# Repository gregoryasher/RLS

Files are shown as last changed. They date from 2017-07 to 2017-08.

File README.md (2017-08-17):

# Remote Lab System: Base Station
The Remote Lab System is a system designed for the University of Washington Bothell campus's Electrical Engineering department. This was a Capstone (or Senior) project that concluded our degrees at the University of Washington. We are a group of Computer Engineering students who were enrolled in the program from 2015 to 2017 when we graduated summer quarter. The development of this project was broken up into Spring and Summer quarter 2017.

# Starting Notes
When we chose this as our project we were initially informed the system did not function. At all. What we found towards the end of our first quarter was the system did not work because previous teams did not create or test any of the components or any code to do so. It became apparent we needed to completely redesign the system and create all the code.

We created a project and work schedule and dove in. These schedules were essential to the success of our project.

# Goals
This was the fourth iteration of the Base Station and our design goals were to: 
Add an additional Intronix LogicPort logic analyzer to support a maximum total of 68-channels
Add an 16-bit Analog-to-Digital Converter (ADC)
Improve heat dissipation from linear regulators
Design a stable chassis
Update Graphical User Interface (GUI)
Improve software robustness

# Purpose
The Remote Lab System is designed to allow students to work on lab experiments remotely away from campus, or the lab facilities. This system is a learning tool and study aid allowing students to have unlimited access, at any time of day, to their required lab equipment. Dr. Arnold Berger at the University of Washington Bothell conducted research showing that when students were given the ability to work remotely, the peak times were between midnight and 4:00 am. His research also concluded that female students spent more time connected to the system than male students, and also generally received higher grades on related course content.

While no version of the Remote Lab System has been officially implemented in coursework, we believe our project will increase students understanding of hardware integration by allowing them to quickly change various settings on daughterboard experiments and observe their changes in real time.

# Conclusion
At the end of our Capstone program in Summer quarter 2017 we had successfully achieved our goals. 

We added an additional logic analyzer: allowing the use of the two operating independently (two 34-channel logic analyzers) or dual support (one 68-channel logic analyzer) based on the configuration of the attached daughterboard.

We added a 16-bit ADC, effectively increasing the accuracy of node voltage measurements made by the system by 256 times.

We successfully solved the heat dissipation issue on the linear regulators by increasing the heatsink size and adding a thermally controlled fan circuit. 

We purchased and built a galvanized steel chassis for the system to be housed, complete with rubber feet to reduce vibrations caused by the fan. The motherboard's daughterboard connectors protrude from the lid such that no daughterboard will have clearance issues on the lid. The motherboard is mounted to the lid using brass standoffs threaded to the lid. The Velleman Oscilloscope/Function Generator system is securely mounted to the bottom of the chassis. Connector cables were made long enough such that the lid may be removed from the chassis and placed flat beside it. The fan is securely mounted to the chassis with no interference on the motherboard and in direct line with all four linear regulator heatsinks.

We successfully updated the GUI to improve security and user lockouts. The user can no longer send updated board information to a daughterboard not installed. The user can no longer change settings on a daughterboard not installed. The user is forced to check which board is installed before making any settings changes. 

The GUI now automatically detects the correct communications port for the Remote Lab System. If the Remote Lab System is not detected upon program start-up, a prompt appears warning the user.

Pressing the "Update Board" button now actually updates the board with the user's desired daughterboard settings.

Pressing the "Check Board" button now actually sends a request to read the daughterboard's boardID pin states. It also receives the correct values that were read.

Linear regulators now have supporting code and the values change based on the constructor's inputs. It should be noted that these devices in previous iterations never operated due to a lack of supporting code.

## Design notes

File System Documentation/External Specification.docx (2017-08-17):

# Remote Lab Station

BCE 496: Capstone Design 2

External Specification

Gregory Asher --- Student ID: 1566775

Gytautas Jankauskas --- Student ID: 1568743

Paolo Sebastian --- Student ID: 1573079

Andrew Soshea --- Student ID: 1321957

Introduction 3

User Guide 3

Hardware Specifications 4

Software Specifications 5

Graphical User Interface (GUI) 5

External Software 6

Operational Requirements 6

# Introduction

The University of Washington Bothell campus is a commuter campus meaning many students commute over a distance (sometimes long) to attend classes. The Remote Lab Station allows students to work on lab experiments at any time and from anywhere.

Using remote desktop applications, a student or faculty member is able to gain access to the Remote Lab Station and run experiments on the plugged in daughter boards. Daughter boards are lab experiments designed by other capstone groups that may give the ability to change node voltages, resistor values, and capacitor values in a circuit.

A user may connect remotely to the Remote Lab System. Upon connecting to the system, they have access to the the hardware on the computer where the Remote lab system is set up. They will have access to the Velleman Oscilloscope and Function Generator and will be able to run tests on real hardware in real time from the comfort of their own home. They will even be able to change values for the tests they are running to make sure they have everything they need to complete their lab.

Due to new restrictions from the UW-IT department, a VPN token (Husky OnNet) is required to connect to the UW campus network remotely. Refer to the UW IT Husky OnNet About Page (https://itconnect.uw.edu/connect/uw-networks/about-husky-onnet/) for more information.

# User Guide

The Remote Lab System Graphical User Interface (GUI) and Arduino software was tested on Windows 7 and Windows 10. We do not guarantee the software’s function on any platform.

In order to connect to use the Remote Lab System the user must connect to the correct campus workstation with the system plugged in. The student should obtain or be provided the workstation’s IP address by a leading faculty member.

Once there, an executable file named “RLS.exe” can be opened and experimentation may begin. To open the Oscilloscope and Function generator software, simply press the “Oscilloscope/Function Generator” button. To open one or both of the LogicPort software, press one of the corresponding “Logic Analyzer” buttons.

Before changing any of the settings in the GUI, a “Check Board” operation must be completed by pressing the “Check Board” button.

The “Update Board” button will again first verify the same board is still installed before sending the desired settings. If the same board is not installed, the user will be warned and updating will not be allowed. Otherwise, after verification, the updated settings will be transmitted to the Arduino.

# Hardware Specifications

- Chassis
  - Size - 10 in x 10 in x 6 in
  - Material - Galvanized Steel
  - Weight - 9lbs
- 2x rear connectors
  - One USB connector
  - One DIN5 power connector
- 1x 80mm Fan
- 4x 40 pin connectors
  - See Figure X for specific pin functions.
- 2-logic Analyzers
  - 68-channels possible
- Velleman Function Generator
  - Amplitude range: 100 mVpp to 10 Vpp @ 1 KHz
  - Offset: from 0 to -5 V or +5 V max
  - 8 bit vertical resolution
  - Sample rate: 12.5 MHz
  - 50 ohm output impedance
  - Frequency range: 0.005 Hz to 500 kHz
- Velleman Oscilloscope
  - Two channel DC bandwidth
  - 1 Mohm / 30 pF Input impedance
  - 30 V maximum input voltage
  - 10 mV to 3V/division input range
  - 0.3 mV display resolution
  - Records 4K samples / channel
  - Sampling frequency of 250 Hz to 25 MHz
- ADS1115 16-bit Analog-to-Digital Converter
  - 4-channels
    - Channel 0: +5 Volts max input
    - Channel 1: +15 Volts max input
    - Channel 2: -5 Volts max input
    - Channel 3: -15 Volts max input
- LT3015 Negative Linear Voltage Regulators
  - -1.22 Volts to -15 Volts output
  - Maximum 0.5 Amp output
  - .14 mV per step
  - Fused from power supply
- LT1963 Positive Linear Voltage Regulators
  - 1.21 Volts to +15 Volts output
  - Maximum 1 Amp output
  - .14 mV per step
  - Fused from power supply
- External power supply
  - Input - 120 VAC
  - Output
    - +15 Volts at 1.5 Amps
    - +5 Volts at 4 Amps
    - -15 Volts at 0.5 Amps
- Temperature range = 0°C - 70°C

# Software Specifications

Students will be able to connect to the RLS workstation via windows remote access to the IP: 128.208.255.52. A user may connect on campus or off campus using the Husky OnNet VPN. One user may to connect to the workstation at a time. On the desktop of the RLS workstation there is an executable file labeled “Remote Lab System”. This opens the RLS graphical user interface (GUI).

### Graphical User Interface (GUI)

Through the GUI, the user is able to check which daughter board is connected, change settings via drop down menus, send updated settings to the Arduino, open the logic analyzer software, and open Velleman oscilloscope software.

When the RLS software is first opened, daughter board settings menus are all deactivated. The only buttons available for interaction are “Check Board”, “Logic Analyzer 1”, and “Logic Analyzer 2”. This prevents a user from changing and applying settings when no daughter board, or a different daughter board, is connected.

A user must click the “Check Board” before any other interaction is possible. If no board is detected or the user has not checked board, then the user will not have permissions to changing any of the settings for any of the boards. Settings may only be changed for a board that is active.

Update board first makes sure that the board that the user is working on is actually the daughter board connected to the Arduino. If it is not, it prompts the user to check board again.

Window resizing including maximizing the screen is possible though the experiment window does not scale with window size.

### External Software

The buttons “Oscilloscope/Function Generator”, “Logic Analyzer”, and “Logic Analyzer 2” open their respective software. This software is provided by the respective manufacturers and is used to take measurements. A user is not allowed to open more than one process of each. If a user attempts to open one that is already open, they are told an instance is already running.

On exit, the software for the logic analyzers and oscilloscope/function generator are also all closed.

# Operational Requirements

In order to operate the system there are some key operational requirements. While this is a remote lab station designed to be used remotely, the Daughterboards must be physically cycled in and out in order for a user to change experiments. This may be done during business hours by a student or a staffed lab technician.

The Remote Lab Station requires an Electrical Engineering lab computer with the Velleman Oscilloscope and Function Generator software, the LogicPort Logic Analyzer software, and our Remote Lab Station software installed. This lab computer should not be used for any purpose other than the Remote Lab Station.

In order for the system to be operational, the Remote Lab Station computer is required to maintain an internet connection and be accessible remotely using the Husky OnNet VPN as required by UW-IT.

The remote lab system has an operating temperature range of 0°C - 70°C. It should be kept in a cool dry place and out of the sunlight. While direct sun exposure should have no effects on the system, the system does generate heat and should have the ventilation ports clear to allow for proper cooling.

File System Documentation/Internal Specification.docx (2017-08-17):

# Remote Lab Station

BCE 496: Capstone 2

Internal Specification

# Abstract

The Remote Lab System is an experimental system designed for electrical engineering students to connect and perform laboratory experiments remotely from off campus. This documentation contains details related to individual component usage including design schematics, algorithms, and graphical interface implementation.

Gregory Asher --- Student ID: 1566775

Gytautas Jankauskas --- Student ID: 1568743

Paolo Sebastian --- Student ID: 1573079

Andrew Soshea --- Student ID: 1321957

Abstract 1

Overall Design 4

Hardware Design 5

Hardware Operation 5

Logic Analyzer 5

Oscilloscope and Function Generator 6

Voltmeter 6

Linear Regulators 9

AD5293 Digital Potentiometers 9

Heat Dissipation 10

Software Design 11

Graphical User Interface (GUI) 11

External Software 12

Arduino 12

readBoardID() 12

Linear Regulator Shutdown 12

Safety Check 12

Daughterboard 13

Linear Voltage Regulator Control 13

Digital Potentiometer Control 13

Test Plan 14

Hardware 14

Individual and Independent Component Test Phase 14

LT1963 (Positive Linear Regulator) 14

LT3015 (Negative Linear Regulator) 15

ADS1115 16-bit ADC (on Adafruit breakout board) 15

AD5293 (Digital Potentiometer) 16

ULN2803A (Darlington Transistor Array) 16

RA30421051 16

LM337 (-5 Volt Regulator) 16

LM317 (+5 Volt Regulator) 16

Motherboard 16

Small Assembly Test Phase 17

Linear Regulator Circuit 17

LM337 and LM317 17

Cooling Circuit 17

Chassis 17

Final Assembly Test Phase 18

Software 19

White Box Software Testing 19

Black Box Software Testing 20

Project Schedule 21

Appendix A: Bill of Materials 22

Appendix B: System Parts List 23

Appendix C 24

# Overall Design

The Remote Lab System (RLS) has four essential components: the motherboard, experimental daughterboards, system enclosure, and dedicated workstation provided by UWB.

The RLS is remotely connected to by students enrolled at the University of Washington using Remote Desktop. Once the student is connected to the campus workstation attached experiments can be run using the RLS GUI. An system overview can be seen in Figure 1.

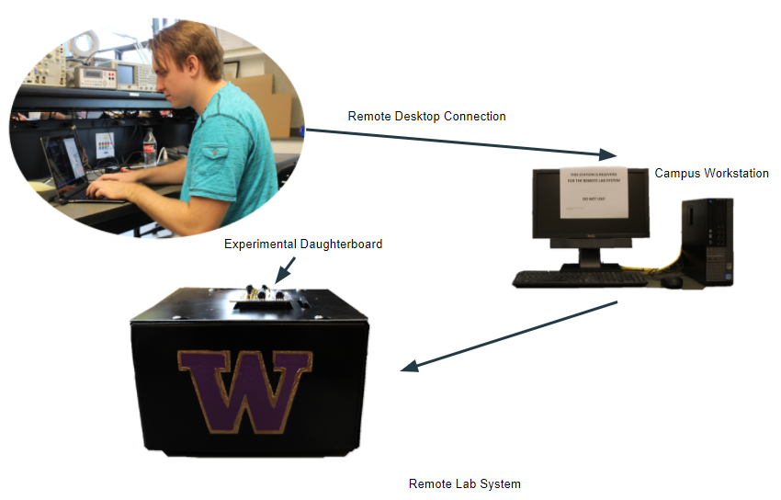
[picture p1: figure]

Figure 1: Overall system layout the Remote Lab System.

Contained within the system enclosure is a USB hub that connects an Arduino Mega 2560, two Intronix logic analyzers, and the Velleman oscilloscope and function generator to the campus workstation. Note: The Arduino Mega 2560 does not obtain power from the USB hub. Experimental boards plug into the RLS using 4 40-pin connectors on the top of the system enclosure.

# Hardware Design

A parts list can be found in Appendix A.

The Remote Lab System is enclosed in a galvanized chassis with a 80mm 2-pin PC fan mounted to the back of the enclosure. There are six connectors visible on the exterior of the chassis: one DIN 5-pin power supply connector, one USB connector, and 4 daughterboard connectors.

The system is powered by a switching mode power supply. This power supply has a DIN 5-pin connector supplying +5V at 4 Amps, -15V at 0.5 Amps, +15V at 1.5 Amps. Each of these pins are protected using a fuse on the motherboard corresponding to their rated voltages. Warning: It is possible to exceed the current limitation of the power supply if multiple linear regulators are used with a low resistance load (less than 1 kΩ). A maximum of one device should be in this mode at any given time.

The motherboard has 4 heat sinks aiding in the cooling of the LT3015 and LT1963 linear regulators. These heat sinks are partnered with an 80mm 5V fan to keep the devices cooled when in high current low voltage output mode.

Mounted to the chassis is a 5V chassis fan.

## Hardware Operation

Components of the motherboard are controlled using an Arduino Mega 2560. Supporting code has been written to control the digital potentiometers allowing users to change the linear regulator outputs. Additionally, supporting code has been written to allow users to control the oscilloscope probe gain. For specific usage of any supporting code, see the Software Operation section.

### Logic Analyzer

The logic analyzers implemented on the motherboard were designed by Intronix. The motherboard simply acts as a mount for these devices and passes the input pins through to the daughterboard connectors. In order to use the two logic analyzers together for a total of 68-channels, the daughterboard must provide a common clock and trigger for both devices. This allows the two logic analyzers to be used independently if desired. A user guide provided by Intronix for using multiple logic analyzers can be found in Appendix C. Additional support for the Intronix logic analyzers can also be found on their website.

### Oscilloscope and Function Generator

The oscilloscope and function generator implemented in the motherboard was designed by Velleman. The motherboard has connector pins allowing the channels of the oscilloscope and function generator to be mechanically fastened and routed to the daughterboard connectors. The scope probe gain adjustment circuit can be seen in Figure 3.

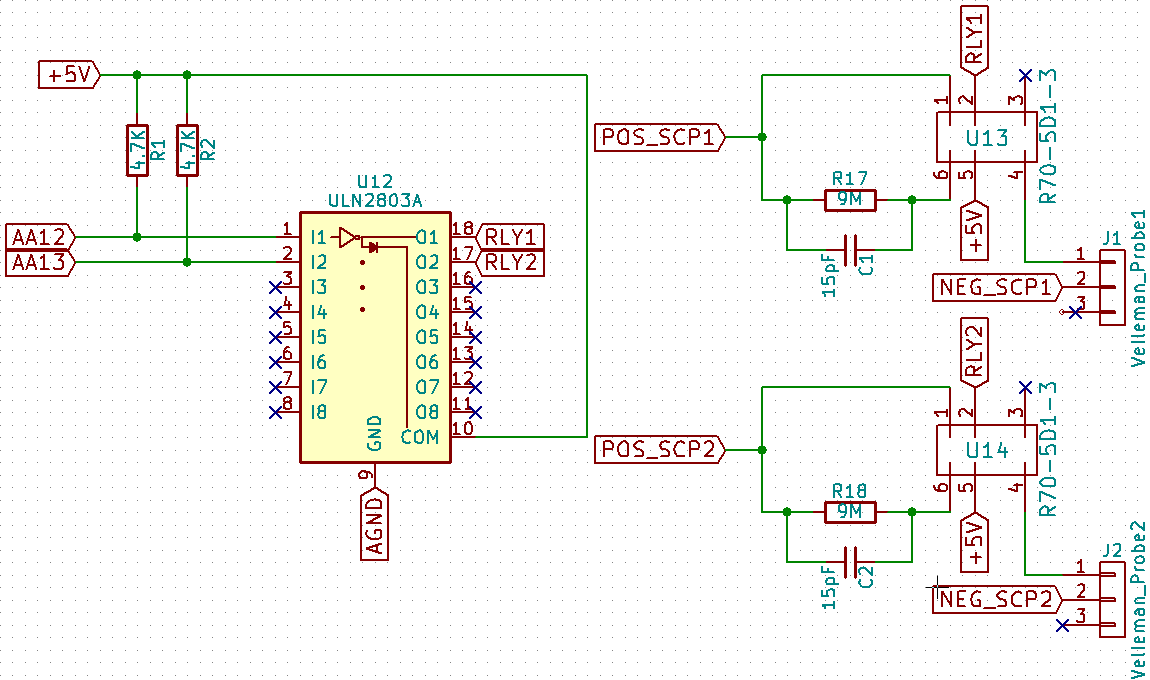
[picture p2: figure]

Figure 2: Scope probe gain schematic.

### Voltmeter

Implemented on the motherboard is an Adafruit ADS1115 4-channel 16-bit ADC. In single ended mode the ADC measures node voltages with respect to ground. The channels operate as follows:

- A0 valid for inputs 0V to +5 Volts
- A1 valid for inputs 0V to +15 Volts
- A2 valid for inputs -5V to 0 Volts
- A3 valid for inputs -15V to 0 Volts

Channels A1 and A3 operate using a voltage division circuit with a ratio of 3.

The voltage divider circuit reduces the voltage seen by the input protecting op-amp by a factor of 3. This allows an experimental board to measure voltages up to 15 volts. After a measurement is taken by the ADC, it is then multiplied by the voltage division ratio in order to obtain the actual value and then displayed to the user on the GUI.

The ADS1115 supports only positive voltages on the input pins in single ended mode so an inverting op-amp on the negative input pins of the ADS1115 (A2 and A3). Before the input voltage is inverted it also goes through a protection buffer with unity gain. The positive channels of the ADS1115 (A0 and A1) has an op-amp configured for unity gain as input protection.

Additional input protection for the ADC comes in the form of Schottky diodes. These diodes remove voltages greater than +5 volts and less than -5 volts. A circuit diagram of the inputs to the ADC can be seen in Figure 4, 5, 6, and 7.

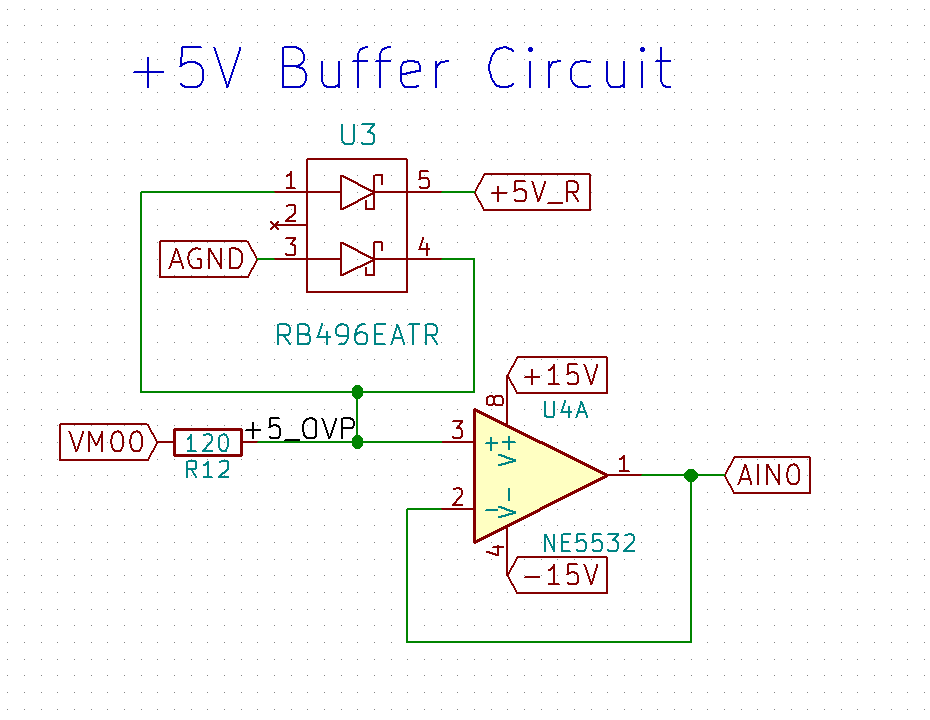
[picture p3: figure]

Figure 3: Positive 5 Volt buffer circuit schematic.

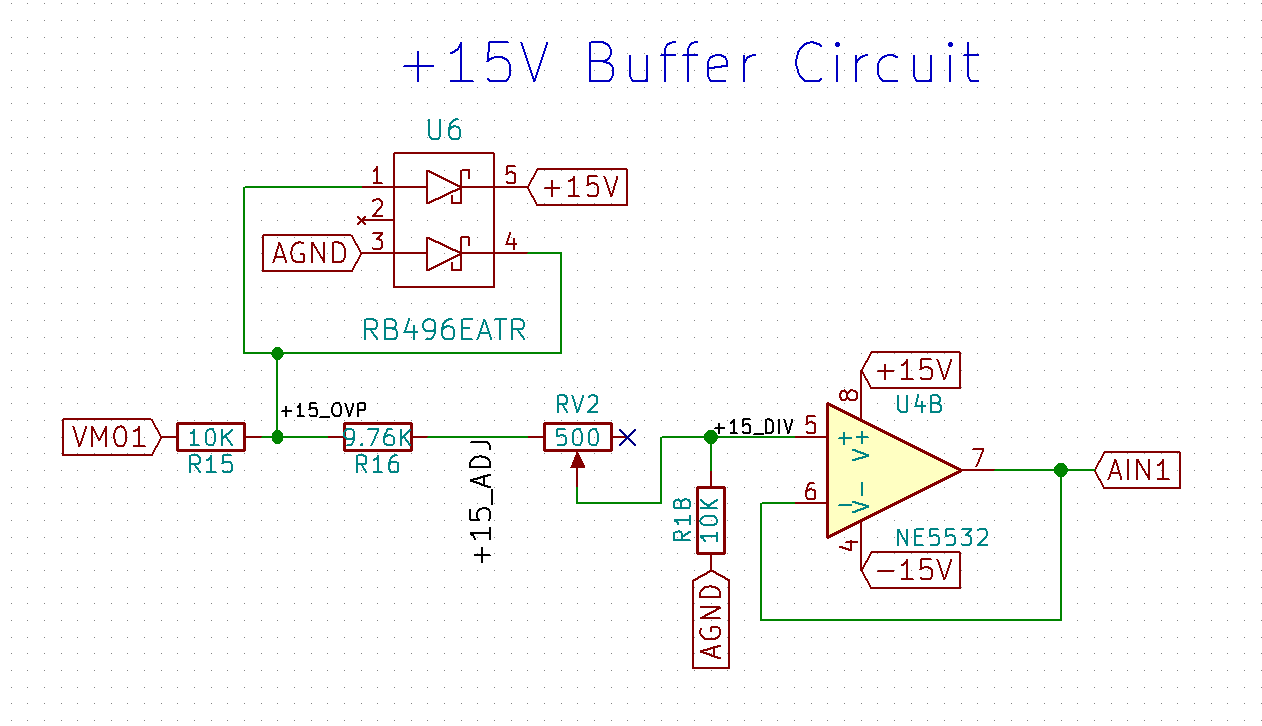
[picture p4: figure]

Figure 4: Positive 15 Volt voltage divider and buffer circuit schematic.

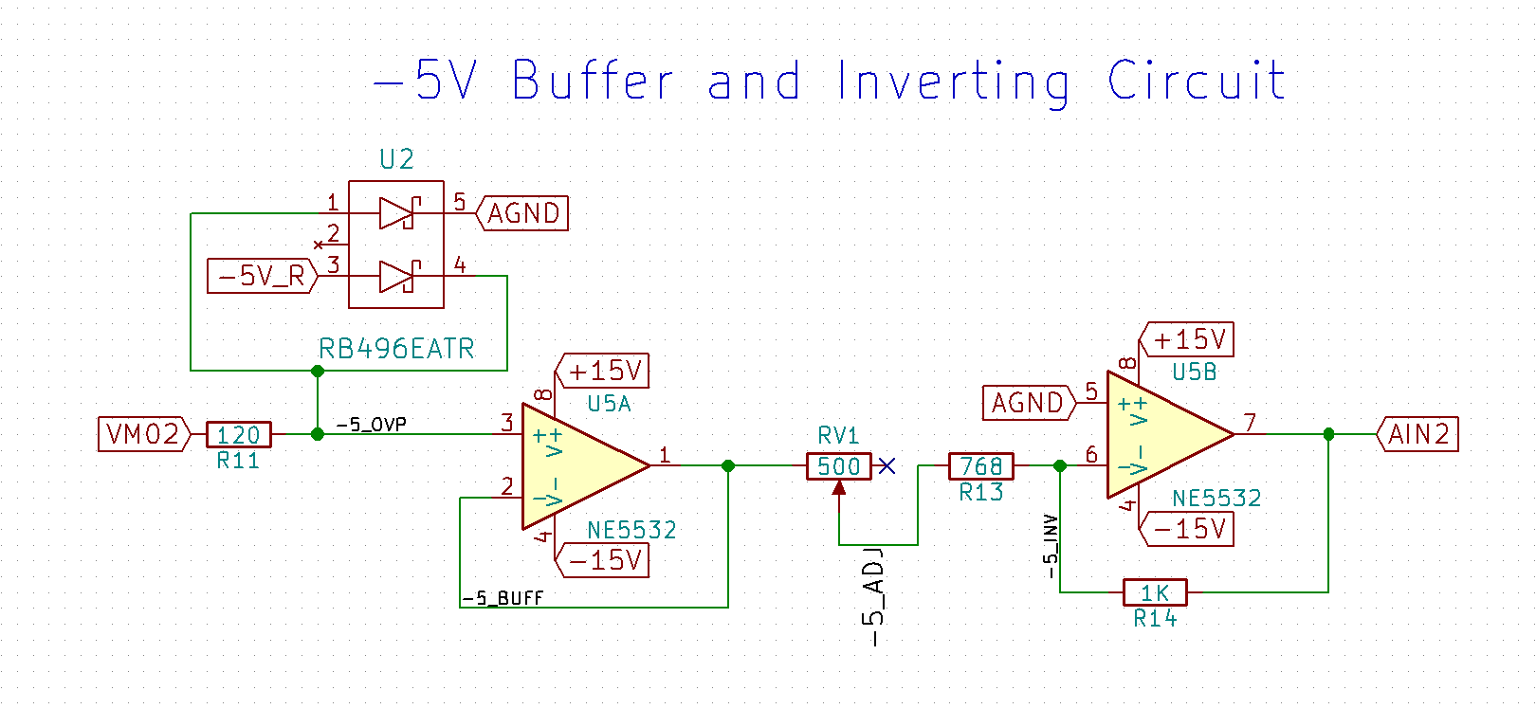
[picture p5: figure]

Figure 5: Negative 5 Volt inverter and buffer circuit schematic.

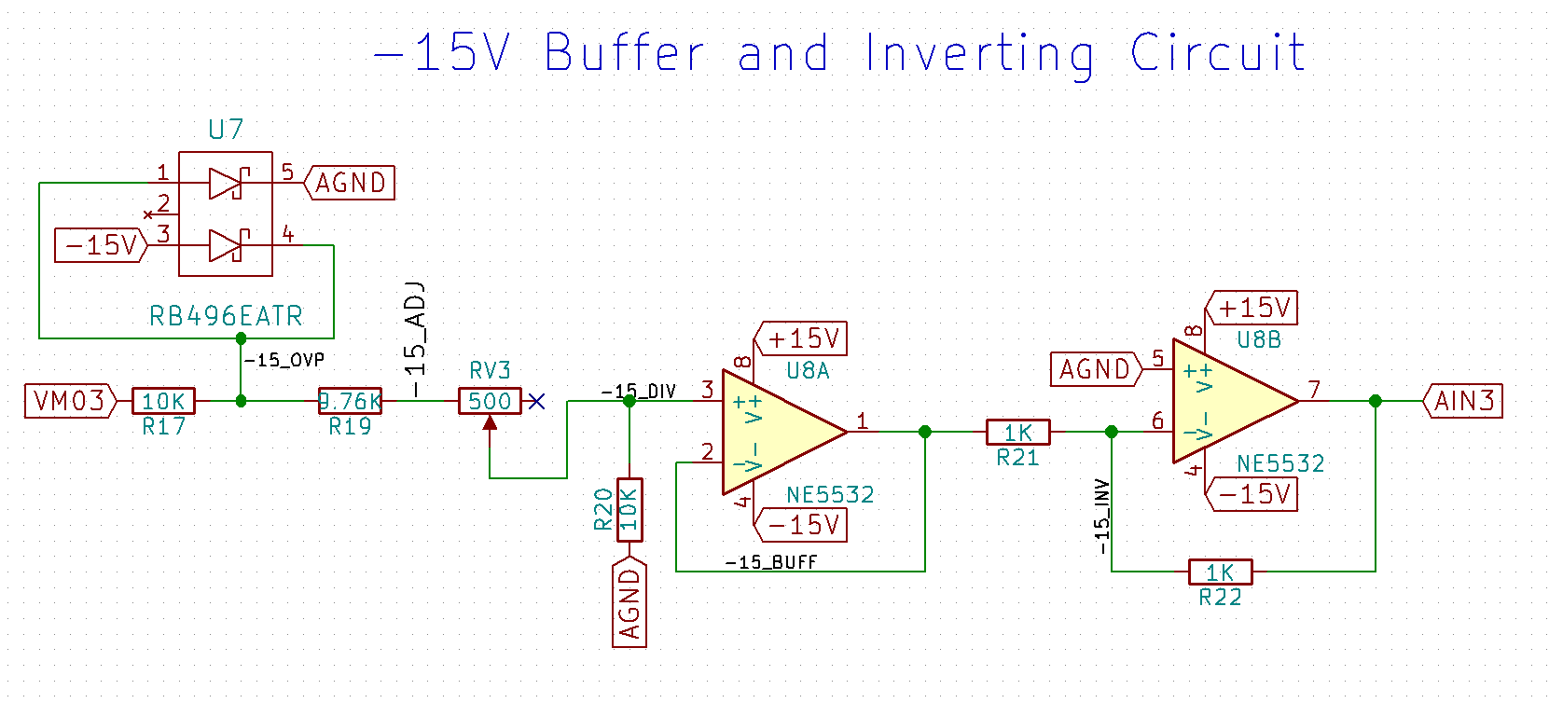
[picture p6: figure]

Figure 6: Negative 15 Volts voltage divider, inverter, and buffer circuit schematic.

### Linear Regulators

The motherboard contains 4 linear regulators: 2 negative regulators (LT3015) and 2 positive regulators (LT1963). A basic schematic, as taken from the datasheets, allowing adjustable operation can be seen in Figure 8 and Figure 9. In place of R2, our implementation has a 20kΩ digital potentiometer (AD5293). The output voltage from the linear regulators is based on the ratio of R1 and R2. With R1 at 1.78kΩ the entire output range of the linear regulators matches the full range of the digital potentiometer.

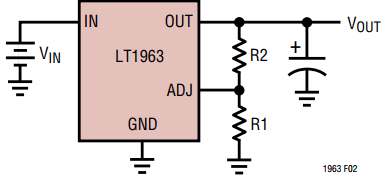
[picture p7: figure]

Figure 7: LT1963 with adjustable output as taken from datasheet.

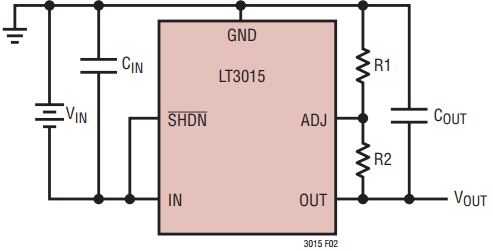
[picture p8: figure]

Figure 8: LT3015 with adjustable output as taken from datasheet.

### AD5293 Digital Potentiometers

Four AD5293 20kΩ digital potentiometers, one for each linear regulator, are used on the motherboard and control linear regulator’s output. The potentiometers are controlled using SPI communication (SPI Mode 1) from the Arduino. The AD5293 has a daisy chaining ability used in the motherboard design, one pair for each linear regulator pair (ie: one daisy chain for both LT3015’s and one daisy chain for both LT1963’s). This requires a 32-bit SPI transfer to change the resistance value.

### Heat Dissipation

The linear regulators are capable of supplying +1.21 Volts from the positive regulator, and -1.22 Volts from the negative regulator. If the attached load is low impedance, high current and high power is generated from the regulator. This heat is dissipated using the heat sinks and fan. Note: Only one linear regulator may be in this low voltage, low output impedance mode at any given time.

The heat sinks used on this motherboard are manufactured by Ohmite and have feet that need to be accounted for in PCB design. These feet should not be connected to any trace and should be isolated.

An 80mm fan is also included in the chassis for the system to force airflow through the heat sink fins. This fan circuit is powered by a MOSFET using a thermistor. The fan circuit diagram can be seen in Figure 10.

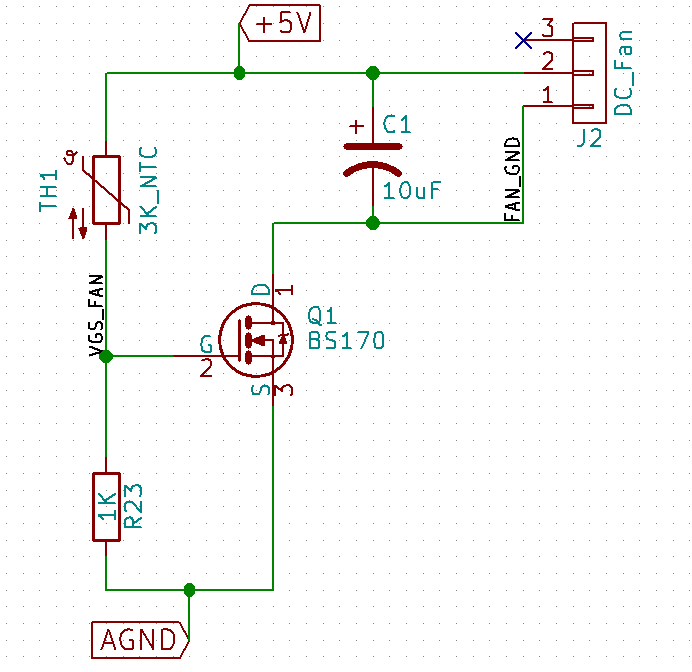
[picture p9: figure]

Figure 9: Fan circuit diagram.

# Software Design

Students will be able to connect to the RLS workstation via windows remote access to the ip: 128.208.255.52. A user may connect on campus or off campus using the Husky OnNet VPN. One user may to connect to the workstation at a time. On the desktop of the RLS workstation there is an executable file labeled “Remote Lab System”. This opens the RLS graphical user interface (GUI).

### Graphical User Interface (GUI)

The GUI is designed and programmed using Windows Forms C#. The GUI is used to communicate with the Arduino using UART serial communication. Through the GUI, the user is able to check which daughterboard is connected, change settings via drop down menus, send the updated settings to the Arduino, open logic analyzer software, and open oscilloscope software.

On startup, the COM port where the RLS system is connected is found and set. This allows the GUI to communicate with the Arduino at the request of the user without the user having to manually find the COM port that the RLS is connected to. This is done by checking all active COM ports and picking out the one the Arduino is connected to.

When the RLS software is first opened, daughterboard settings menus are deactivated using a deactivate function. The only buttons available for interaction are “Check Board”, “Logic Analyzer”, and “Logic Analyzer 2”. This prevents a user from changing and applying settings when no daughterboard, or a different daughterboard is connected.

A user must click the “Check Board” before any other interaction is possible. If no board is detected or the user has not checked board, then the user will not have permissions to changing any of the settings for any of the boards. Settings may only be changed for a board that is active. Check board works by sending “boardID” to the Arduino via the UART protocol. The Arduino then sends back the ID of the daughterboard currently connected. Based on the board connected, the panel for the test for that specific daughterboard is then enabled.

The “Update Board” button first verifies the daughterboard the user is attempting to update is still connected to the Remote Lab System. If it is not, the GUI prompts the user to press “Check Board” again. If the correct daughterboard is still connected, “Update Board” compiles the user’s settings into a String based on the state of the drop down menus and bubble options. After the String is created it is transmitted to the Arduino using Universal Asynchronous Receiver/Transmitter (UART).

Window resizing including maximizing the screen is possible though the experiment window does not scale with window size. This is due to previously designed experiment windows.

### External Software

The buttons “Oscilloscope/Function Generator”, “Logic Analyzer”, and “Logic Analyzer 2” open their respective software. The software is opened via hard coded file paths. This software is provided by the manufacturer and is used to take measurements. A user is not allowed to open more than one process of each. If a user attempts to open one that is already open, they are told an instance is already running.

On exit, the software for the logic analyzers and oscilloscope/function generator are also all closed. The windows are closed using the process.kill() command provided in C#.

### Arduino

On power on or after reset, the Arduino reads the boardID of a connected daughterboard, shuts down the linear regulators, and executes supporting daughterboard code (if one is connected). After it performs these setup functions the Arduino waits for data to be received from the GUI. The GUI sends data in the form of a String such as boardID, or a daughterboard settings String to be interpreted by supporting daughterboard code.

#### readBoardID()

If the String sent by the GUI is equivalent to “boardid” the Arduino reads the boardID pins (configured to be pins A0 - A7 on the Arduino) using digitalRead(). The boardID pins will read 1111_1111 if no daughterboard is connected (ie: the boardID pins are tied high). The read 8-bit boardID is converted to a string and is sent to the GUI using Universal Asynchronous Receiver/Transmitter (UART).

#### Linear Regulator Shutdown

The linear regulators have a logical shutdown pin that is toggled using the Arduino. The shutdown is commonly triggered when changing daughterboards or when no board is detected.

#### Safety Check

The purpose of the safety check function is to constantly check the state of the boardID pins. If the boardID pins change states the linear regulators are shut down.

#### Daughterboard

Each daughterboard has a supporting C++ class that configures the Arduino’s digital pins to its own unique specification. This class is called upon when updating the board using the “Update Board” button in the GUI. The GUI sends a String via UART containing information passed onto the class.

In order to determine which daughterboard class to call, the Arduino first creates a substring to determine which board it is receiving information for. The daughterboard class then further dissects the String sent by the GUI to set digital pins on the Arduino.

#### Linear Voltage Regulator Control

A daughterboard can manipulate a total of four DC voltage sources, two negative and two positive. The Arduino adjusts the voltages of the regulators by manipulating digital potentiometers attached to each regulator. Voltages are set using a constructor with the desired voltage(s) taken as parameters. The constructor takes the desired output voltage value and calculates the required digital potentiometer resistance using one of the equations below.

The calculation used for setting the positive regulator values can be seen in Equation 1.

The calculation used for setting the negative regulator values can be seen in Equation 2.

Equation 1: Potentiometer (Ω)=(V_(OUT) - 1.21V)/((1.21V)/(1.78kΩ) + 3µA)

Equation 2: Potentiometer (Ω)=(V_(OUT) + 1.22V)/((-1.22V)/(1.78kΩ) + 30nA)

#### Digital Potentiometer Control

The digital potentiometer acts as a controllable resistor to adjust the linear voltage regulators. In order for the digital potentiometer to set its wiper to the calculated resistance value, the resistance must first be digitally converted into 20 Ω increments to complement the 1024-position resolution of the AD5293 digital potentiometers. This was accomplished using Equation 3.

Equation 3: Digital Resistance (Ω) =(R_(POT))/(20000.0 Ω)⋅1024.0 positions

Once the required digital resistance is calculated, the wipers for the digital potentiometers are enabled and they are sent a complete 16-bit data-word using SPI. This 16-bit word is composed of two unused bits followed by four command bits that control the operation of the digital potentiometer and finally the 12 data bits which contain the calculated digital resistance position that the digital potentiometer wiper needs to be set to. As the digital potentiometers are daisy chained, the data needed to be sent twice (for a total of 32 bits being sent) in order to reach both potentiometers. When the data has been sent and the potentiometers are set, the output voltage of the linear regulators are subsequently changed once they are turned back on.

# Test Plan

The test plan is broken down into two separate categories, Hardware and Software.

## Hardware

The hardware section is split into testing phases. The individual and independent component phase is testing that is done solely using a single component at a time. The small assembly testing phase is testing done incorporating small components together and testing their connected usages. Final assembly testing is performed after the entire PCB is assembled.

### Individual and Independent Component Test Phase

The individual and independent component test phase refers to the testing of each individual device received. We tested each device for expected operation and usage. The goal of this testing phase is to learn and experiment with device operations.

#### LT1963 (Positive Linear Regulator)

- Tested in adjustable output mode example circuit from datasheet. (See Figure 8)
  - Observed output range from 1.21 Volts to 15 Volts using manually adjustable pot and 1.78kΩ 1% resistor.
    - Calculated expected output value using Equation 1.
- Observed high amp output (with 1Ω load resistor).
  - Noted in this mode risk of blowing power supply fuse.
  - Daughterboards should use caution when using the regulators in this mode. Power supply has 1.5 Amp rating. One device is capable of producing a >1 Amp draw alone.
- Tested power generation and heat dissipation with heatsinks
  - Noted temperatures uncooled >55°C
  - Device rated for 70°C
  - Determined air cooling necessary in order to obtain high amperage outputs.

#### LT3015 (Negative Linear Regulator)

- Tested in adjustable output mode using example circuit from datasheet (See Figure 9)
  - Observed output range from -1.22 Volts to -15 Volts using manually adjustable pot and 1.78kΩ 1% resistor.
    - Calculated expected output value using Equation 2.
  - Observed high amp output (with 1Ω load resistor).
    - Noted in this mode high risk of blowing power supply fuse.
    - Daughterboards should use caution when using the regulators in this mode. Power supply has 0.5 Amp rating. One device is capable of producing a >1 Amp draw alone.
- Tested power generation and heat dissipation with heatsinks
    - Noted temperatures uncooled >55°C
    - Device rated for 70°C
    - Determined air cooling necessary when in high amp output mode.

#### ADS1115 16-bit ADC (on Adafruit breakout board)

- Tested single ended and differential input modes
  - Observed negative voltages unreadable in single ended mode.
  - Observed built in protection circuit functionality.
    - When applying voltages out of range of the ADC, reads max range. When pushed further past readings on other channels misbehave.
  - Observed higher gain states at lower input voltages for more accurate voltage measurement.
- Tested single ended mode with voltage divider, buffer, and inverting amplifier
  - Observed accurate reading with voltage divider and buffer circuits.
    - Compared Serial Monitor readings with multimeter
  - Observed accurate readings with inverted negative voltage inputs.
    - Compared Serial Monitor readings with multimeter
    - Will need to be inverted in the software for user view
- Tested auto gain adjustments in software
  - Used power supply and multimeter to observe resolution changes.

#### AD5293 (Digital Potentiometer)

- Tested basic functions of a single device
  - Device operates using SPI communication
    - SPI Mode 1
  - Observed reset operation
    - Noted on reset the wiper moves to half (10kΩ)
  - Observed resistance change based on hex values
    - Single device requires a 16-bit transfer
    - 10-bits are data (1023 possible wiper positions)
    - Each data bit accounts for ~20Ω
- Tested daisy chain capabilities
  - Requires 32-bit data transfer to write and update both devices
  - Observed resistance changes of both devices in series
    - Despite 32-bit transfer doesn’t appear slower

#### ULN2803A (Darlington Transistor Array)

- Tested outputs given 5 Volt inputs
  - Expected output currents large enough to drive inductive load
    - Able to toggle RA30421051 Relay

#### RA30421051

- Tested with DC power supply and pull up resistor
- Tested for continuity on switching poles
  - Expected switch to throw on 5 Volt logic

#### LM337 (-5 Volt Regulator)

- Tested with DC power supply with 15 Volt input
  - Expected consistent +5 Volt output

#### LM317 (+5 Volt Regulator)

- Tested with DC power supply with -15 Volt input
  - Expected consistent -5 Volt ouput

#### Motherboard

- Upon arrival performed visual inspection of quality
- Upon arrival measured resistance at all power nodes to all ground nodes.
  - Expected reading: Overload

### Small Assembly Test Phase

The small assembly test phase refers to the testing of multiple components tied together in a similar manner that will be used in the final implementation.

#### Linear Regulator Circuit

Two LT3015 and two LT1963 linear voltage regulators used in combination with 4 AD5293 digital potentiometers. For the two LT3015 negative linear voltage regulators two AD5293 digital potentiometers are daisy chained together.

- Tested voltage changes based on digital pot value changes
  - Observed full voltage output range (-15 Volts to -1.22 Volts)
- Tested software controller for changing voltage values
  - Observed correct operation based on function parameters
  - Function takes in a desired voltage and uses an algorithm to determine required digital potentiometer value

#### LM337 and LM317

- Tested to ensure expected output
  - Observed +15 Volt regulated down to +5 Volt output
    - Noted higher currents possible with lower impedance loads.
  - Observed -15 Volt regulated down to -5 Volt output
    - Noted higher currents possible with lower impedance loads.

#### Cooling Circuit

The cooling circuit operates using a BS170 N-Channel MOSFET, a thermistor, and a 5V 2-pin 80mm fan. The fan is implemented to encourage airflow along the heat sinks for the linear voltage regulators.

- Tested fan circuit with potentiometer to simulate thermistor
  - Expected to voltage drop across transistor to increase, thus turning on the fan
  - Observed fan operation

#### Chassis

- Tested connection fitment
- Tested daughterboard connector fitment against lid

### Final Assembly Test Phase

The final assembly test phase refers to testing after construction of the entire PCB (ie: all components have been soldered to the board). This testing is also performed after chassis modification has been completed.

- Tested motherboard spacer fitment on lid
  - Daughterboard connectors protrude from lid as expected
  - Reasonable connector clearance
  - Minimal flex experienced when attaching/detaching a daughterboard
- Tested connection to logic analyzer cards
  - Logic analyzers securely fastened to motherboard
  - Logic analyzer’s USB connector is accessible
- Tested Velleman connections
  - Mechanical probe connections are secure
  - Oscilloscope appropriately displays waveform
    - Waveform generated by Tektronix AFG3252 Waveform Generator
    - Waveform passed into scope via daughterboard oscilloscope probe pins
  - Function Generator produces acceptable waveform
    - Waveform measured by Tektronix MSO3012 Mixed Signal Oscilloscope
    - Waveform measured from daughterboard connector pin
- Tested USB hub connectivity with work station
  - Velleman is detected via USB hub
    - Velleman software receives hardware response
  - Logic analyzers are detected via USB hub
    - LogicPort software detects both devices independently
  - Arduino is detected via USB hub
    - Arduino detected by Arduino IDE
    - Communicates with GUI
- Test linear voltage regulator outputs
  - Positive regulators
    - Expected output ranges between 1.22 Volts and 15 Volts
    - Expected steady output at specified value
      - Measured using Keithley Multimeter
  - Negative regulators
    - Expected output ranges between -15 Volts and -1.23 Volts
    - Expected steady output at specified value
      - Measured using Keithley Multimeter
- Tested heat dissipation performance
  - Expected fan to power on when heat is detected
  - Expected device(s) to continue operating (ie: device does not enter shut down mode)
  - Device remains within operating temperature range
- Tested boardID detection
  - Expected 1111_1111 reading with no daughterboard connected
  - Simulated boardID’s using Keithley DC power supply

## Software

The Remote Lab System Graphical User Interface (GUI) and Arduino software was tested on Windows 7 and Windows 10. We do not guarantee the software’s function on any platform.

Software testing occurs in multiple stages throughout the development process and was performed both as White Box testing and Black Box testing. White box testing was used for evaluating the performance of code used for controlling essential devices. Black box testing was used to ensure limitations on user access and control of the system.

### White Box Software Testing

- Tested collection of user settings
  - Expected GUI to generate a String with user settings
  - Expected GUI to transmit created string using UART to Arduino
- Tested user lockout methods
  - Expected user can only change values of the active board
  - Expected all drop down menus inaccessible when no board detected
  - Expected warning message if no board detected
  - Required successful boardID check before settings can be changed
  - Only single instances of applications allowed
- Tested application shutdown on GUI exit
  - Expected LogicPort and Velleman software to terminate on GUI exit
- Tested communication from GUI to Arduino
  - User settings on the experiments page are correctly sent to the Arduino
    - Arduino handles these UART signals and passes them correctly to the corresponding daughterboard experiment C++ file.
  - boardID request sent via UART to Arduino
    - Arduino responds with boardID read from analog pins
- Tested automatic detection of RLS Arduino
  - Expected automatic port setting for Serial communication
- Tested Arduino control of linear regulators
  - Uses daisy chained AD5293 digital potentiometers
  - Expected outputs from LT3015 negative linear regulators to be from -15 Volts to -1.22 Volts
    - Error returned on out-of-range inputs
  - Expected outputs from LT1963 negative linear regulators to be from 15 Volts to 1.21 Volts
    - Error returned on out-of-range inputs
- Tested ADS1115 (ADC) control
  - Expected less than 1% margin of error
    - Simulated using Keithley DC power supply
    - Compared readings with Keithley multimeter
  - Expected single ended single readings
- Tested Arduino safety functions
  - Arduino shuts down linear regulators on GUI exit
  - Arduino shuts down linear regulators when no boardID detected

### Black Box Software Testing

- Tested Graphical User Interface (GUI)
  - User is unable to change settings when daughterboard is not detected
  - User is only able to change settings on detected daughterboard screen
  - Software closes upon closing of the RLS GUI
  - User is only able one instance of each program
  - User can change detected daughterboard’s settings and observe correct output corresponding with the input settings

# Project Schedule

Schedule for Capstone 1:

| Category | Milestone | Due Date
1. | Documentation | Determine Parts to be Used | May 19th 2017
2. | Documentation | Final Contract | June 9th 2017
3. | Documentation | Final Project Specification | June 9th 2017

Schedule for Capstone 2:

| Category | Milestone | Due Date
1. | Hardware & Software | Demonstrate New Motherboard Design | July 28th 2017
2. | Hardware & Software | Integrate Daughterboards with Motherboard | July 28th 2017
3. | Documentation | Final Report | August 18th 2017
4. | Documentation | Final Presentation | August 18th 2017

# Appendix A: Bill of Materials

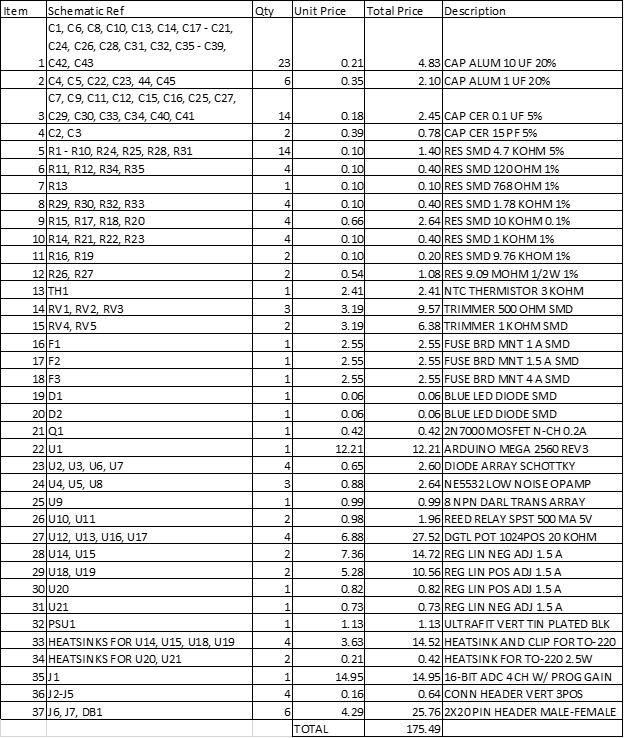
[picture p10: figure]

# Appendix B: System Parts List

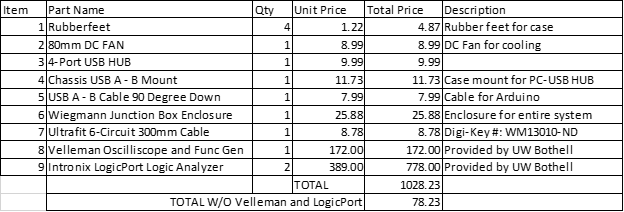
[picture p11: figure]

# Appendix C

The following is copied from a .txt file provided by Intronix on the usage of multiple logic analyzers together.

As mentioned in the FAQs, it is recommended to use multiple units in state mode if your circuit can provide a common clock and trigger signal to all units. The common clock is what keeps the samples coherent in time, while the common trigger signal is what synchronizes the acquisitions of multiple units.

It is possible to use multiple units in timing mode, but keep in mind that each unit has its own independent clock oscillator. Since the clocks are not synchronized this means that at the trigger sample there will be an uncertainty of +/-1 sample period between units. This effectively reduces the timing resolution by 1/2 (500MHz only has resolution of 250MHz). With compression enabled, the situation can get even worse since it may be possible to compress large numbers of samples into the buffer. While the uncertainty at the trigger point is always +/-1 sample period, the clock oscillators have a worst case mismatch of 100ppm between multiple units. If you were able to compress 1,000,000 samples into the buffer, the signals sampled 1,000,000 sample periods before/after the trigger event could have a differential error of 100 sample periods between units! This is why we don't recommend using multiple units in timing mode. Often times you won't be able to capture (or even be interested in) 1,000,000 samples, so this last point isn't always an issue.

Here are a few tips on using multiple LogicPorts from one PC:

1. The LogicPort software will open the first LogicPort it finds. The first instance of the software you open will use the first LogicPort you connected to the PC. Once that instance is open, the second instance of the software will find and use the second LogicPort connected and so on.

2. It will be more convenient if you have separate installations of the LogicPort software so that each instance has it's own .INI file in it's respective install directory. The .INI file tells the software which project file to open when the application starts up (among other things). The default installation is in:

"C:\Program Files\LogicPort"

We recommend that you install the second instance in a directory such as:

"C:\Program Files\LogicPort2"

3. Here's the tricky part: The second installation will overwrite the desktop and start menu shortcuts causing them to point to the second installation only. You will need to create a new shortcut which points to the first installation. You should be able to just make a copy of the desktop shortcut and change the shortcut's target directory to point to the first installation.

Note that although there should be separate installations, you don't necessarily need to use separate directories for project or export files. For example, you could open a project file in the "\Projects" directory of the first installation using the second instance of the software.

We have run as many as 4 LogicPorts from the same PC simultaneously, and the theoretical limit is 127 units.

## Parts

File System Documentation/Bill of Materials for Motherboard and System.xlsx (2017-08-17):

Item | Schematic Ref | Qty | Unit Price | Total Price | Description | Part Name | Digi-Key Part # | Manufacuter | Package/Case | Link
1 | C1, C6, C8, C10, C13, C14, C17 - C21, C24, C26, C28, C31, C32, C35 - C39, C42, C43 | 23 | 0.21 | 4.83 | CAP ALUM 10 UF 20% |  | PCE3895CT-ND | Panasonic Electronic Components | RADIAL SMD 4x5.3mm | https://www.digikey.com/products/en?keywords=PCE3895CT-ND | Greg | Gytatus | Paolo | Andrew
2 | C4, C5, C22, C23, 44, C45 | 6 | 0.35 | 2.10 | CAP ALUM 1 UF 20% |  | PCE4024CT-ND | Panasonic Electronic Components | RADIAL SMD 4x5.3mm | https://www.digikey.com/products/en?keywords=PCE4024CT-ND | 110 | 130 | 120 | 100
3 | C7, C9, C11, C12, C15, C16, C25, C27, C29, C30, C33, C34, C40, C41 | 14 | 0.17 | 2.45 | CAP CER 0.1 UF 5% |  | 399-1250-1-ND | KEMET | 1206 | https://www.digikey.com/products/en?keywords=399-1250-1-ND
4 | C2, C3 | 2 | 0.39 | 0.78 | CAP CER 15 PF 5% |  | 490-9071-1-ND | Murata Electronics NA | THRU-HOLE | https://www.digikey.com/product-detail/en/murata-electronics-north-america/RDE5C2A150J0S1H03A/490-9071-1-ND/4772233
5 | R1 - R10, R24, R25, R28, R31 | 14 | 0.10 | 1.40 | RES SMD 4.7 KOHM 5% |  | 311-4.7KERCT-ND | Yageo | 805 | https://www.digikey.com/product-detail/en/yageo/RC1206JR-074K7L/311-4.7KERCT-ND/732242
6 | R11, R12, R34, R35 | 4 | 0.10 | 0.40 | RES SMD 120 OHM 1% |  | P120FCT-ND | Panasonic Electronic Components | 1206 | https://www.digikey.com/products/en?keywords=P120FCT-ND
7 | R13 | 1 | 0.10 | 0.10 | RES SMD 768 OHM 1% |  | P768FCT-ND | Panasonic Electronic Components | 1206 | https://www.digikey.com/products/en?keywords=P768FCT-ND
8 | R29, R30, R32, R33 | 4 | 0.10 | 0.40 | RES SMD 1.78 KOHM 1% |  | P1.78KFCT-ND | Panasonic Electronic Components | 1206 | https://www.digikey.com/products/en?keywords=P1.78KFCT-ND
9 | R15, R17, R18, R20 | 4 | 0.66 | 2.64 | RES SMD 10 KOHM 0.1% |  | P10KBCCT-ND | Panasonic Electronic Components | 1206 | https://www.digikey.com/products/en?keywords=P10KBCCT-ND
10 | R14, R21, R22, R23 | 4 | 0.10 | 0.40 | RES SMD 1 KOHM 1% |  | P1.00KFCT-ND | Panasonic Electronic Components | 1206 | https://www.digikey.com/products/en?keywords=P1.00KFCT-ND
11 | R16, R19 | 2 | 0.10 | 0.20 | RES SMD 9.76 KHOM 1% |  | P9.76KFCT-ND | Panasonic Electronic Components | 1206 | https://www.digikey.com/products/en?keywords=P9.76KFCT-ND
12 | R26, R27 | 2 | 0.54 | 1.08 | RES 9.09 MOHM 1/2W 1% |  | PPCHF9.09MCT-ND | Vishay BC Components | THRU-HOLE | https://www.digikey.com/product-detail/en/vishay-bc-components/HVR3700009094FR500/PPCHF9.09MCT-ND/720088
13 | TH1 | 1 | 2.41 | 2.41 | NTC THERMISTOR 3 KOHM |  | 615-10008-ND | US Sensor | THRU-HOLE | https://www.digikey.com/products/en/sensors-transducers/temperature-sensors-ntc-thermistors/508?k=615-1008-ND
14 | RV1, RV2, RV3 | 3 | 3.19 | 9.57 | TRIMMER 500 OHM SMD |  | 490-2671-1-ND | Bourns Inc | J LEAD SMD | https://www.digikey.com/products/en?keywords=490-2671-1-ND
15 | RV4, RV5 | 2 | 3.19 | 6.38 | TRIMMER 1 KOHM SMD |  | 490-2660-1-ND | Bourns Inc | J LEAD SMD | https://www.digikey.com/products/en?keywords=490-2660-1-ND
16 | F1 | 1 | 2.55 | 2.55 | FUSE BRD MNT 1 A SMD |  | F1222CT-ND | Littelfuse Inc | 2-PAD SMD | https://www.digikey.com/products/en/circuit-protection/fuses/139?k=F1222CT-ND
17 | F2 | 1 | 2.55 | 2.55 | FUSE BRD MNT 1.5 A SMD |  | F1223CT-ND | Littelfuse Inc | 2-PAD SMD | https://www.digikey.com/products/en/circuit-protection/fuses/139?k=F1223CT-ND
18 | F3 | 1 | 2.55 | 2.55 | FUSE BRD MNT 4 A SMD |  | F1227CT-ND | Littelfuse Inc | 2-PAD SMD | https://www.digikey.com/product-detail/en/littelfuse-inc/0154004.DR/F1227CT-ND/183376
19 | D1 | 1 | 0.06 | 0.06 | BLUE LED DIODE SMD |  |  | Chanzon | 603 | https://www.amazon.com/Chanzon-Colors-100pcs-Emitting-Yellow/dp/B01CUGA380
20 | D2 | 1 | 0.06 | 0.06 | BLUE LED DIODE SMD |  |  | Chanzon | 603 | https://www.amazon.com/Chanzon-Colors-100pcs-Emitting-Yellow/dp/B01CUGA380
21 | Q1 | 1 | 0.42 | 0.42 | 2N7000 MOSFET N-CH 0.2A | 2N7000 | 2N7000TACT-ND | Fairchild/ON Semiconductor | TO-92 | https://www.digikey.com/product-detail/en/fairchild-on-semiconductor/2N7000TA/2N7000TACT-ND/3042479
22 | U1 | 1 | 12.21 | 12.21 | ARDUINO MEGA 2560 REV3 |  |  | Elegoo | SEE PCB FOOTPRINT | https://www.amazon.com/Elegoo-Board-ATmega2560-ATMEGA16U2-Arduino/dp/B0719HSWQ4?s=electronics
23 | U2, U3, U6, U7 | 4 | 0.65 | 2.60 | DIODE ARRAY SCHOTTKY | 2 Indep Schottky | RB496EACT-ND | Rohm Semiconductor | SOT-23-5 | https://www.digikey.com/products/en?keywords=RB496EACT-ND
24 | U4, U5, U8 | 3 | 0.88 | 2.64 | NE5532 LOW NOISE OPAMP | NE5532 | 296-13622-1-ND | Texas Instruments | SOIC-8 | https://www.digikey.com/products/en?keywords=296-13622-1-ND
25 | U9 | 1 | 0.99 | 0.99 | 8 NPN DARL TRANS ARRAY | ULN2803A | 497-2356-5-ND | STMircoelectronics | DIP-18 | https://www.digikey.com/product-detail/en/stmicroelectronics/ULN2803A/497-2356-5-ND/599591
26 | U10, U11 | 2 | 0.98 | 1.96 | REED RELAY SPST 500 MA 5V | HE721A0500 | HE100-ND | Littelfuse Inc | DIP-14 | https://www.digikey.com/product-detail/en/littelfuse-inc/HE721A0500/HE100-ND/133183
27 | U12, U13, U16, U17 | 4 | 6.88 | 27.52 | DGTL POT 1024POS 20 KOHM | AD5293 | AD5293BRUZ-20-RL7CT-ND | Analog Devices Inc | TSSOP-14 | https://www.digikey.com/product-detail/en/analog-devices-inc/AD5293BRUZ-20-RL7/AD5293BRUZ-20-RL7CT-ND/3790133
28 | U14, U15 | 2 | 7.36 | 14.72 | REG LIN NEG ADJ 1.5 A | LT3015 | LT3015IT#PBF-ND | Linear Technology | TO-220-5 | https://www.digikey.com/products/en?keywords=LT3015IT%23PBF-ND
29 | U18, U19 | 2 | 5.28 | 10.56 | REG LIN POS ADJ 1.5 A | LT1963 | LT1963ET#PBF-ND | Linear Technology | TO-220-5 | https://www.digikey.com/products/en?keywords=LT1963ET%23PBF-ND
30 | U20 | 1 | 0.82 | 0.82 | REG LIN POS ADJ 1.5 A | LM317 | LM317TFS-ND | Fairchild/ON Semiconductor | TO-220-3 | https://www.digikey.com/products/en?keywords=LM317TFS-ND
31 | U21 | 1 | 0.73 | 0.73 | REG LIN NEG ADJ 1.5 A | LM337 | LM337TFS-ND | Fairchild/ON Semiconductor | TO-220-3 | https://www.digikey.com/products/en?keywords=LM337TFS-ND
32 | PSU1 | 1 | 1.13 | 1.13 | ULTRAFIT VERT TIN PLATED BLK | On-board Power Plug | WM11778-ND | Molex, LLC | SEE PCB FOOTPRINT | https://www.digikey.com/products/en?keywords=WM11778-ND
33 | HEATSINKS FOR U14, U15, U18, U19 | 4 | 3.63 | 14.52 | HEATSINK AND CLIP FOR TO-220 | LARGE HEATSINK | C220-025-1AE-ND | Ohmite | SEE PCB FOOTPRINT | https://www.digikey.com/products/en?keywords=C220-025-1AE-ND
34 | HEATSINKS FOR U20, U21 | 2 | 0.21 | 0.42 | HEATSINK FOR TO-220 2.5W | LOW PROFILE HS | HS115-ND | Aavid Thermalloy |  | https://www.digikey.com/product-detail/en/aavid-thermalloy/507302B00000G/HS115-ND/5849
35 | J1 | 1 | 14.95 | 14.95 | 16-BIT ADC 4 CH W/ PROG GAIN | ADS1115 |  | Adafruit | 1X10 HEADER 2.54mm Pitch | https://www.adafruit.com/product/1085
36 | J2-J5 | 4 | 0.16 | 0.64 | CONN HEADER VERT 3POS |  | A19470-ND | TE Connectivity AMP Connectors | 1X3 HEADER 2.54mm Pitch
37 | J6, J7, DB1 | 6 | 4.29 | 25.76 | 2X20 PIN HEADER MALE-FEMALE |  |  |  | 2X20 HEADER 2.54mm Pitch | https://www.amazon.com/gp/product/B01ITMN6K6
 |  |  | TOTAL | 175.49
Item | Part Name | Qty | Unit Price | Total Price | Description | Link
1 | Rubberfeet | 4 | 1.22 | 4.87 | Rubber feet for case | https://www.amazon.com/gp/product/B003B0YDRM
2 | 80mm DC FAN | 1 | 8.99 | 8.99 | DC Fan for cooling | https://www.amazon.com/gp/product/B00ZFPDAI4
3 | 4-Port USB HUB | 1 | 9.99 | 9.99 |  | https://www.amazon.com/gp/product/B00XMD7KPU
4 | Chassis USB A - B Mount | 1 | 11.73 | 11.73 | Case mount for PC-USB HUB | https://www.amazon.com/gp/product/B003VSXQVI
5 | USB A - B Cable 90 Degree Down | 1 | 7.99 | 7.99 | Cable for Arduino | https://www.amazon.com/gp/product/B0716WBP9R
6 | Wiegmann Junction Box Enclosure | 1 | 25.88 | 25.88 | Enclosure for entire system | https://www.newegg.com/Product/Product.aspx?Item=9SIA5D52J56093
7 | Ultrafit 6-Circuit 300mm Cable | 1 | 8.78 | 8.78 | Digi-Key #: WM13010-ND | https://www.digikey.com/products/en?keywords=WM13010-ND
8 | Velleman Oscilliscope and Func Gen | 1 | 172.00 | 172.00 | Provided by UW Bothell | https://www.amazon.com/Velleman-PCSGU250-Usb-Pc-Scope-Generator/dp/B006DXCO3E
9 | Intronix LogicPort Logic Analyzer | 2 | 389.00 | 778.00 | Provided by UW Bothell | https://www.pctestinstruments.com/order.htm
 |  |  | TOTAL | 1028.23
 | TOTAL W/O Velleman and LogicPort |  |  | 78.23

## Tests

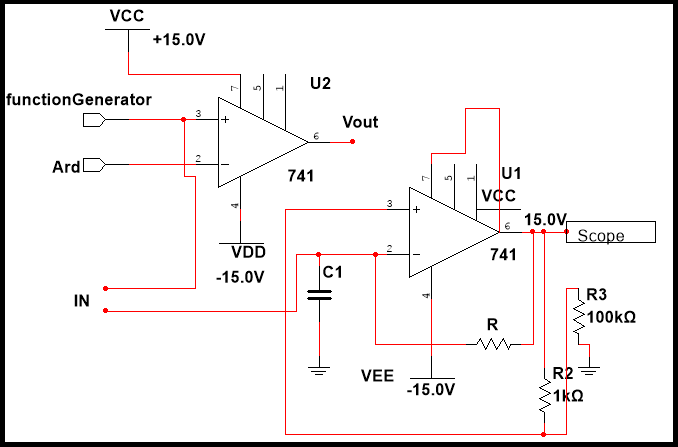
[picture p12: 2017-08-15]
RLSinC#/Remote_EE_Lab/Remote_EE_Lab/Resources/Experiment 93.png

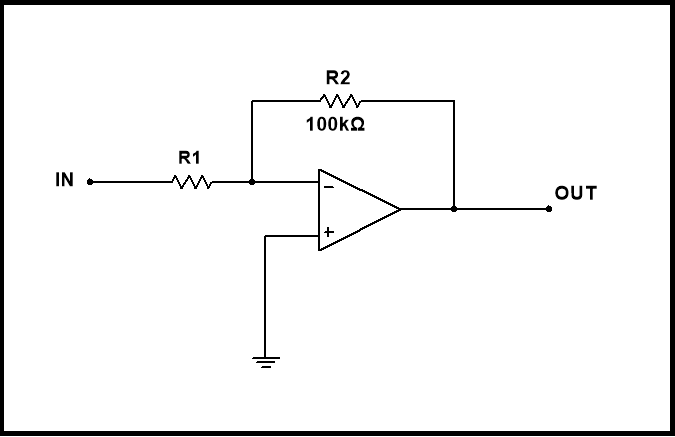
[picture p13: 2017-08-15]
RLSinC#/Remote_EE_Lab/Remote_EE_Lab/Resources/Experiment 11.png

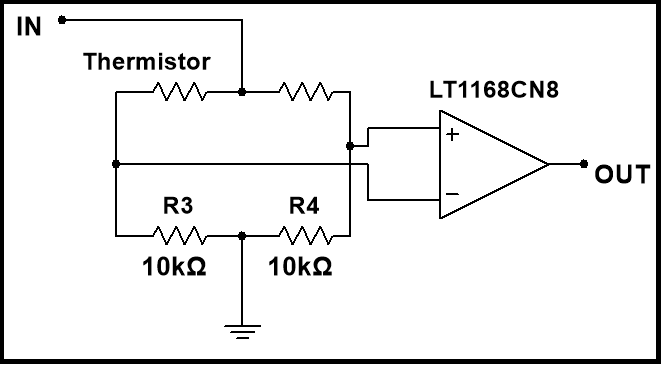
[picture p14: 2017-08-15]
RLSinC#/Remote_EE_Lab/Remote_EE_Lab/Resources/Experiment 81.png

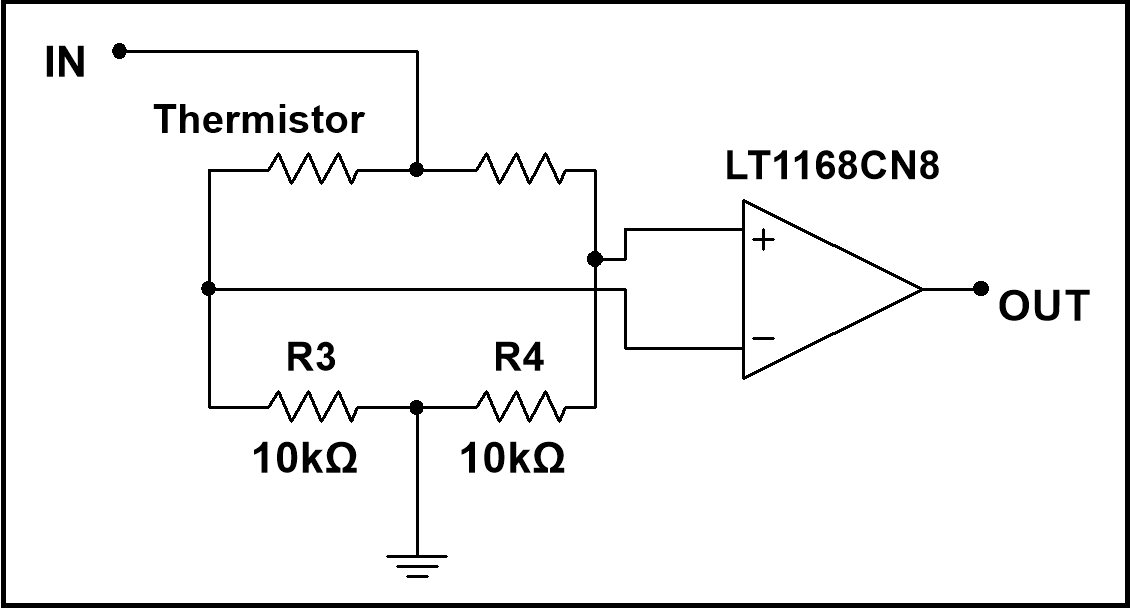
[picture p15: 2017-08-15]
RLSinC#/Remote_EE_Lab/Remote_EE_Lab/Resources/Experiment 8.png

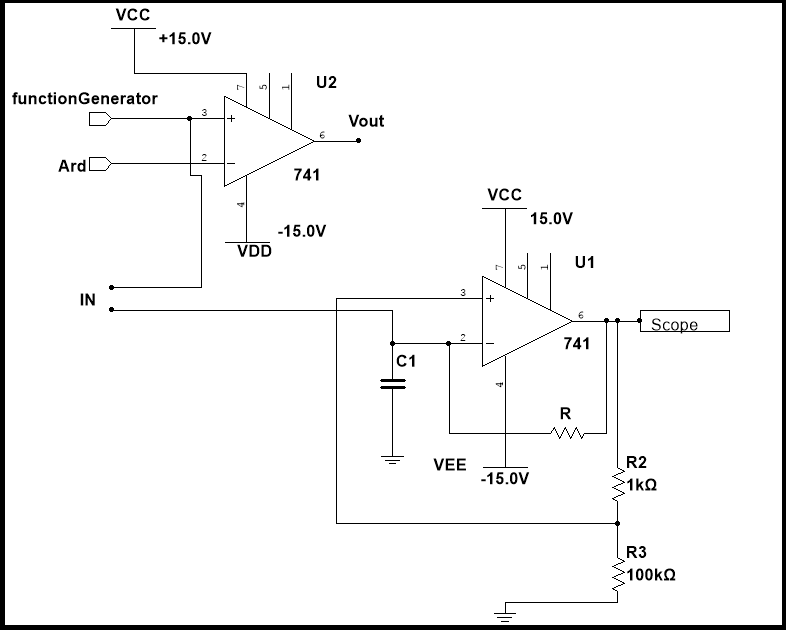
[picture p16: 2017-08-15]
RLSinC#/Remote_EE_Lab/Remote_EE_Lab/Resources/Experiment 9.png

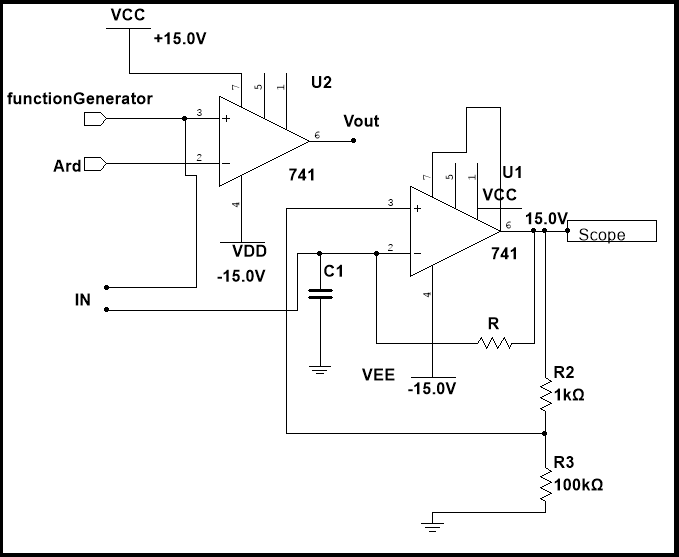
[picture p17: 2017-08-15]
RLSinC#/Remote_EE_Lab/Remote_EE_Lab/Resources/Experiment 91.png

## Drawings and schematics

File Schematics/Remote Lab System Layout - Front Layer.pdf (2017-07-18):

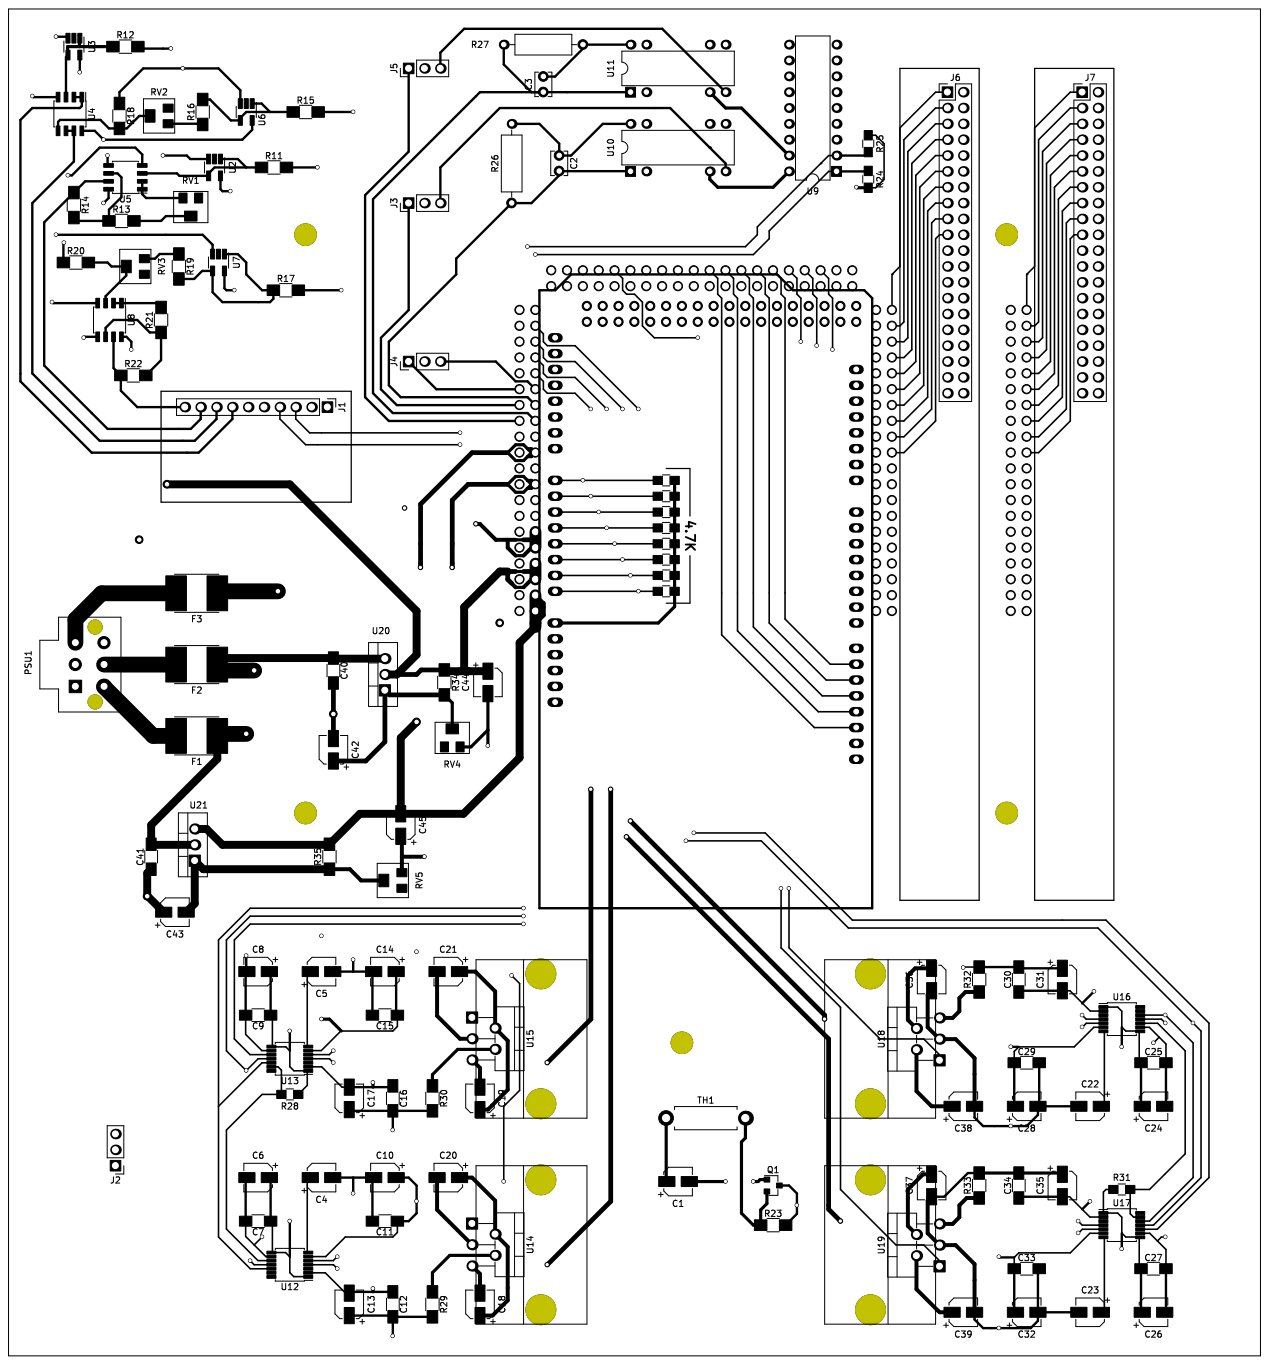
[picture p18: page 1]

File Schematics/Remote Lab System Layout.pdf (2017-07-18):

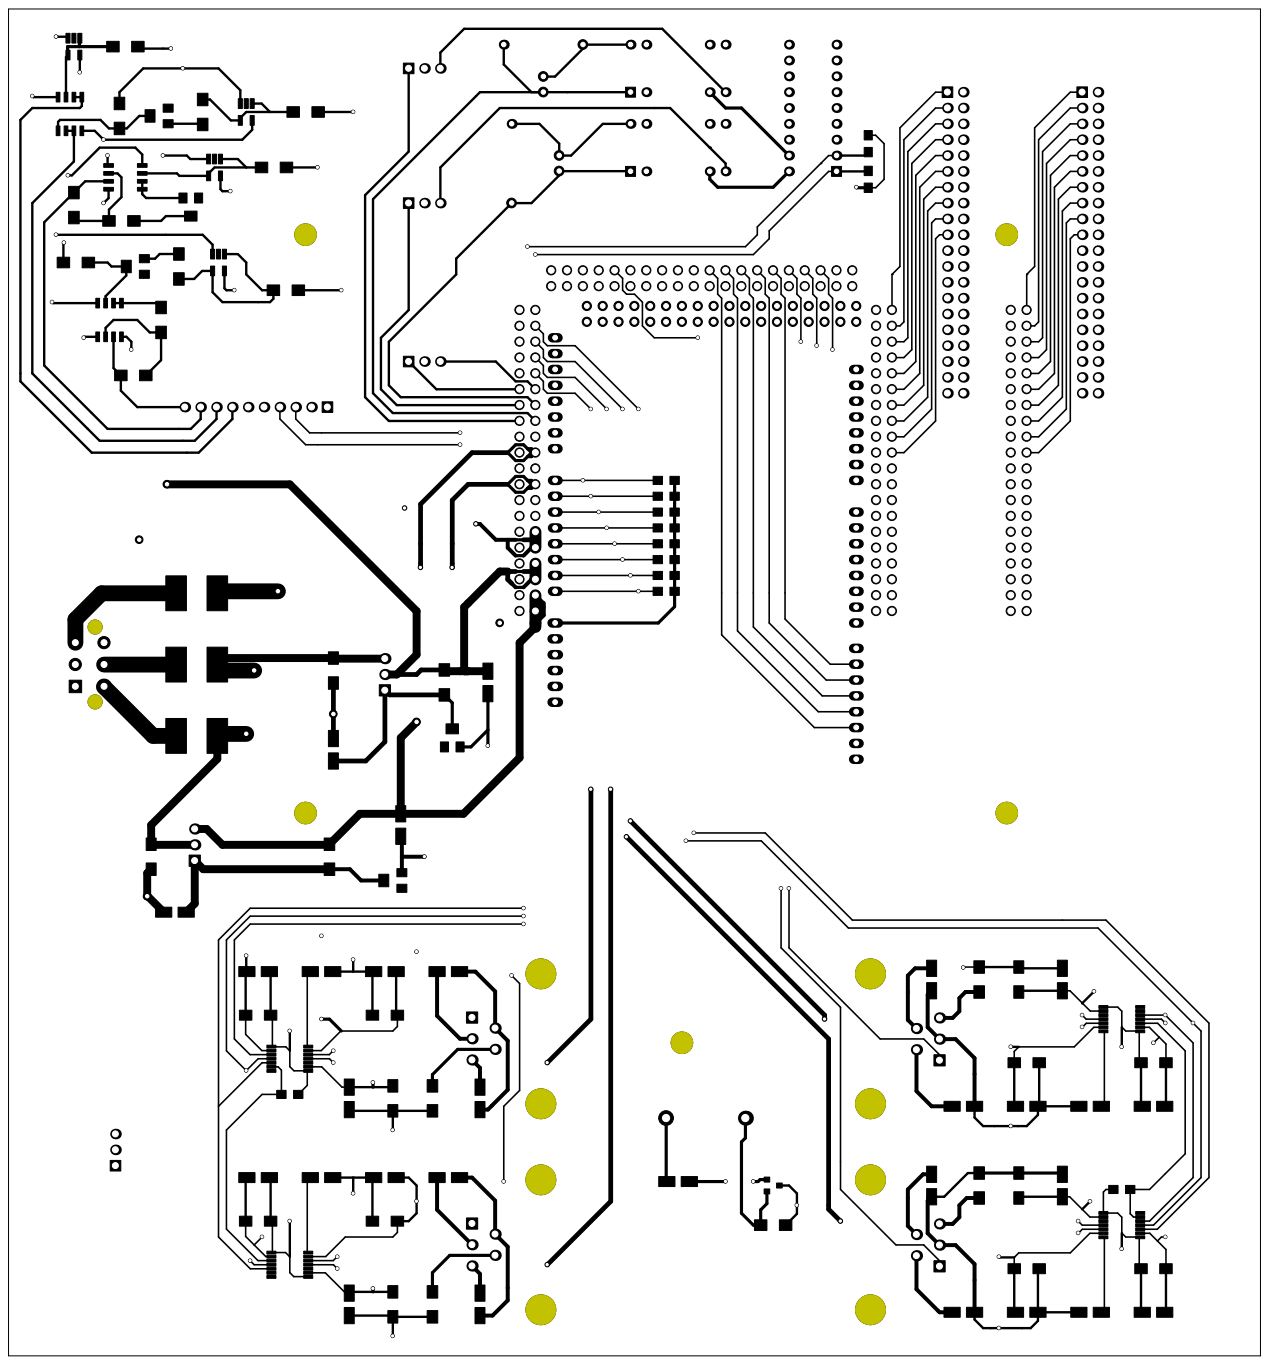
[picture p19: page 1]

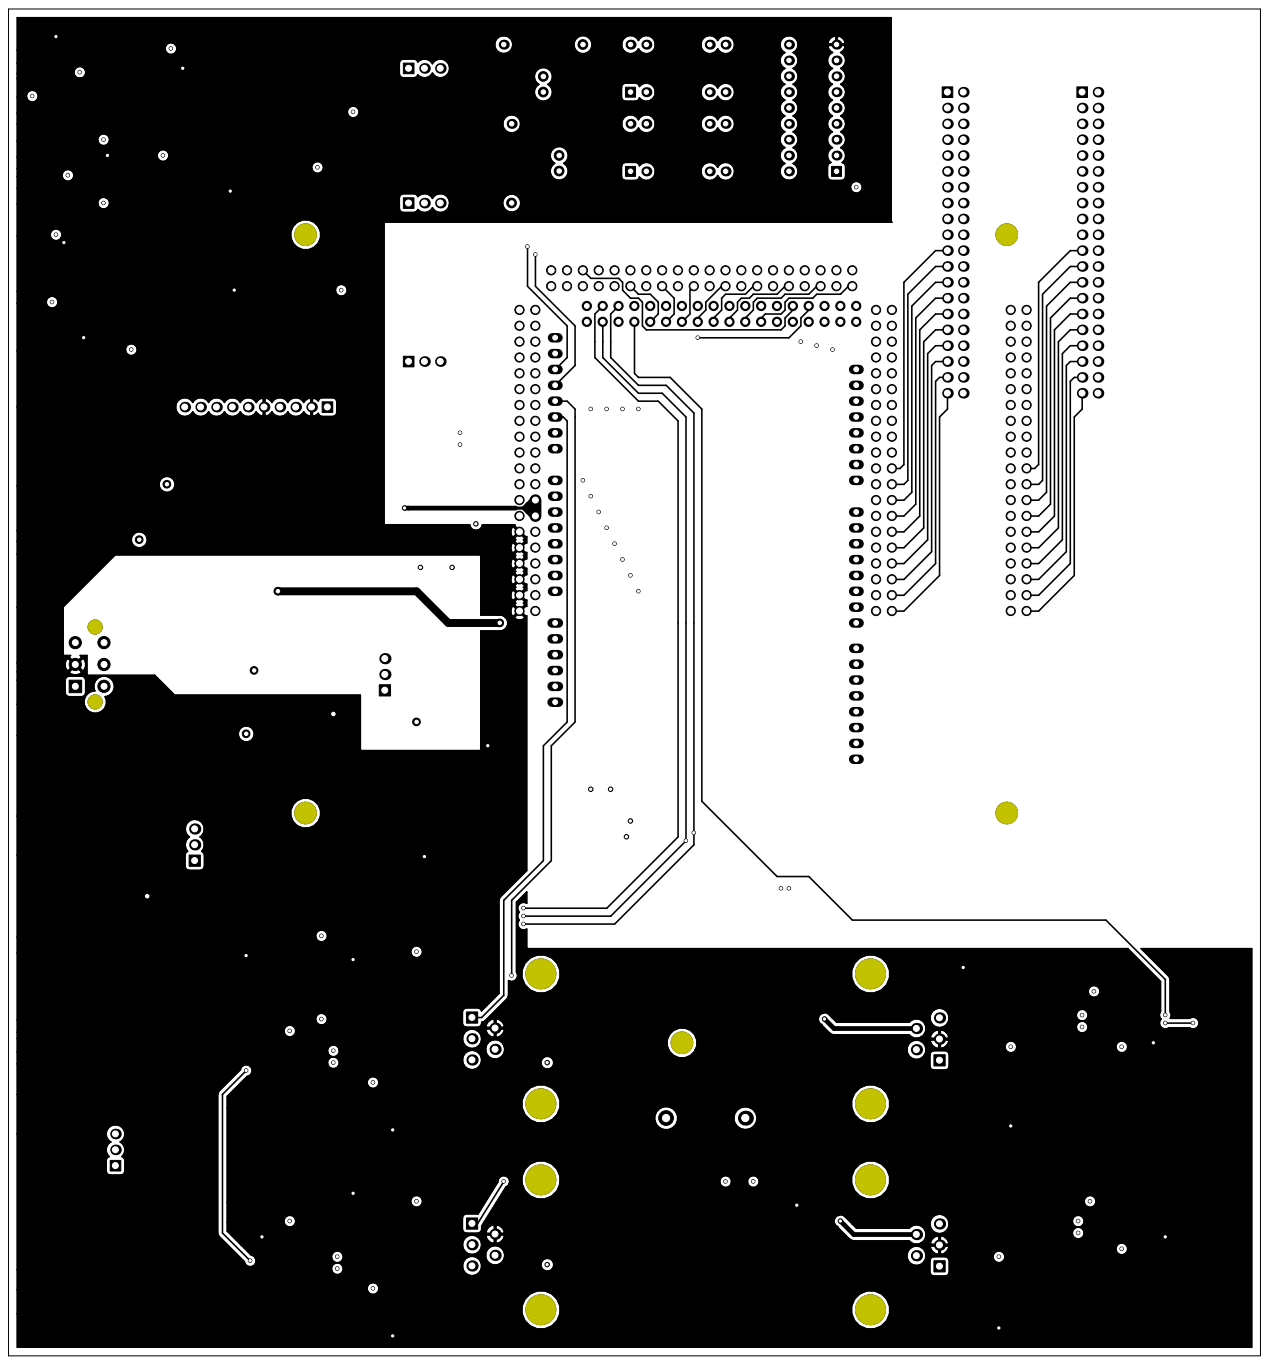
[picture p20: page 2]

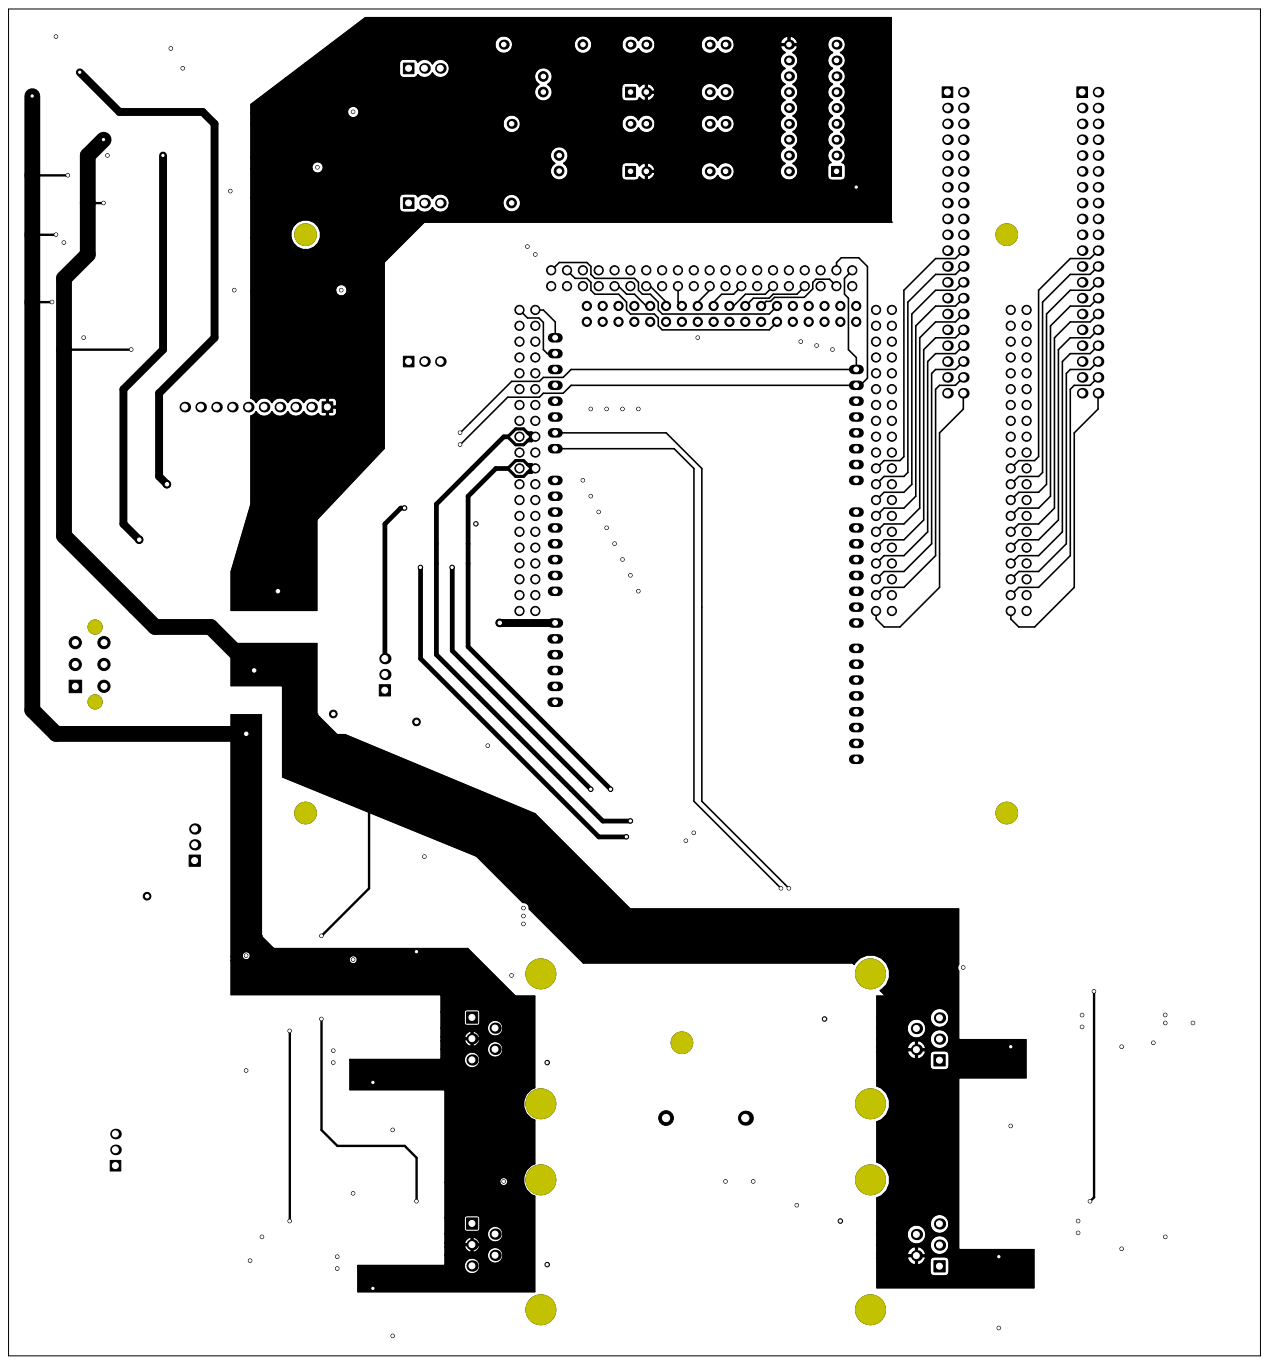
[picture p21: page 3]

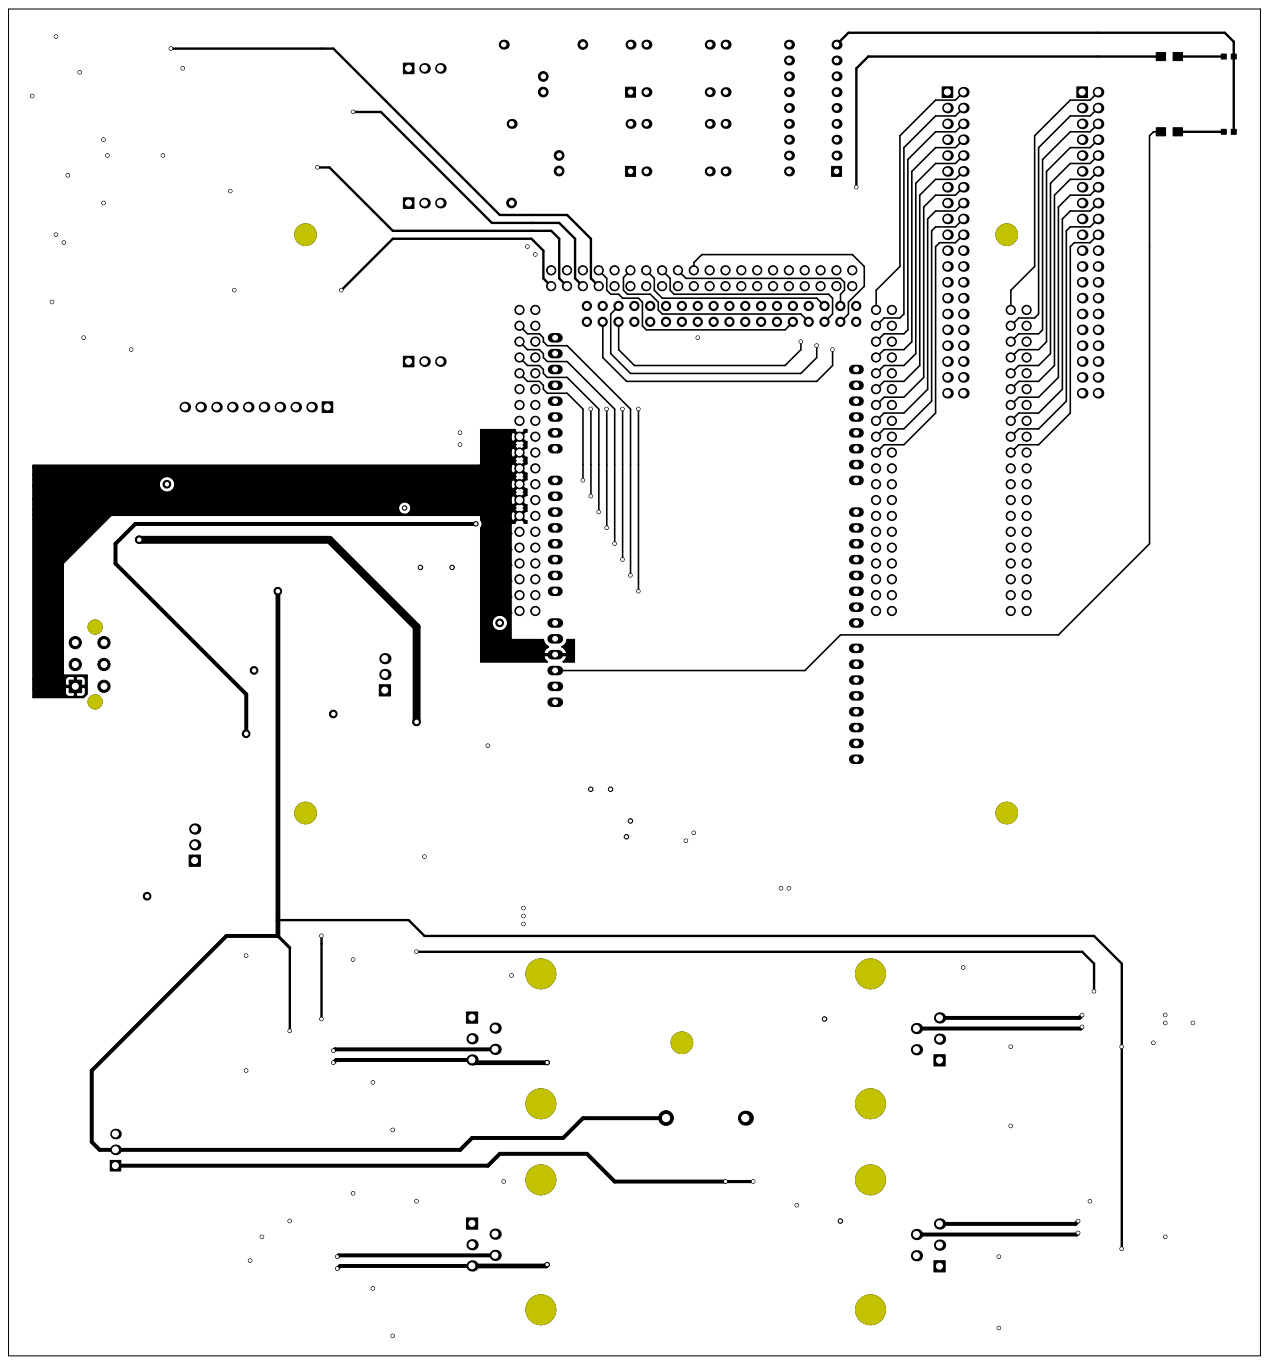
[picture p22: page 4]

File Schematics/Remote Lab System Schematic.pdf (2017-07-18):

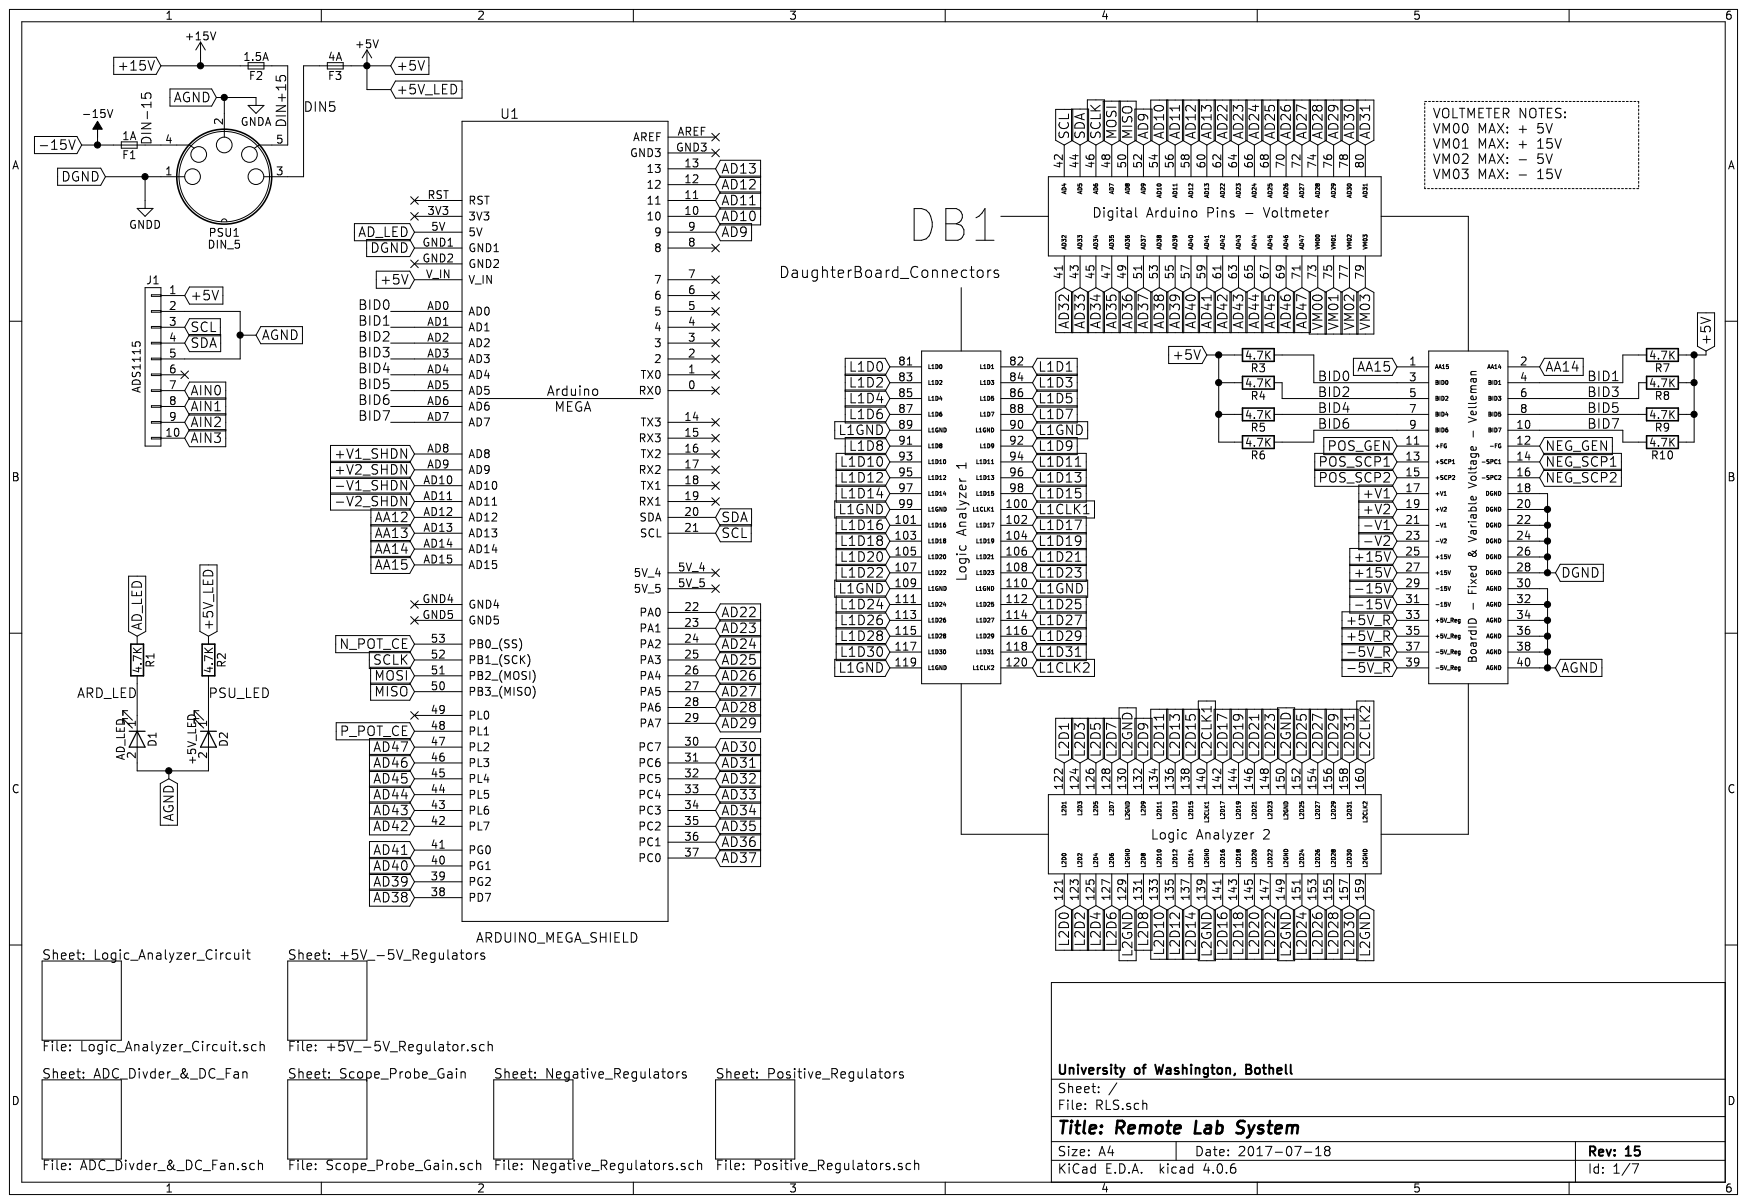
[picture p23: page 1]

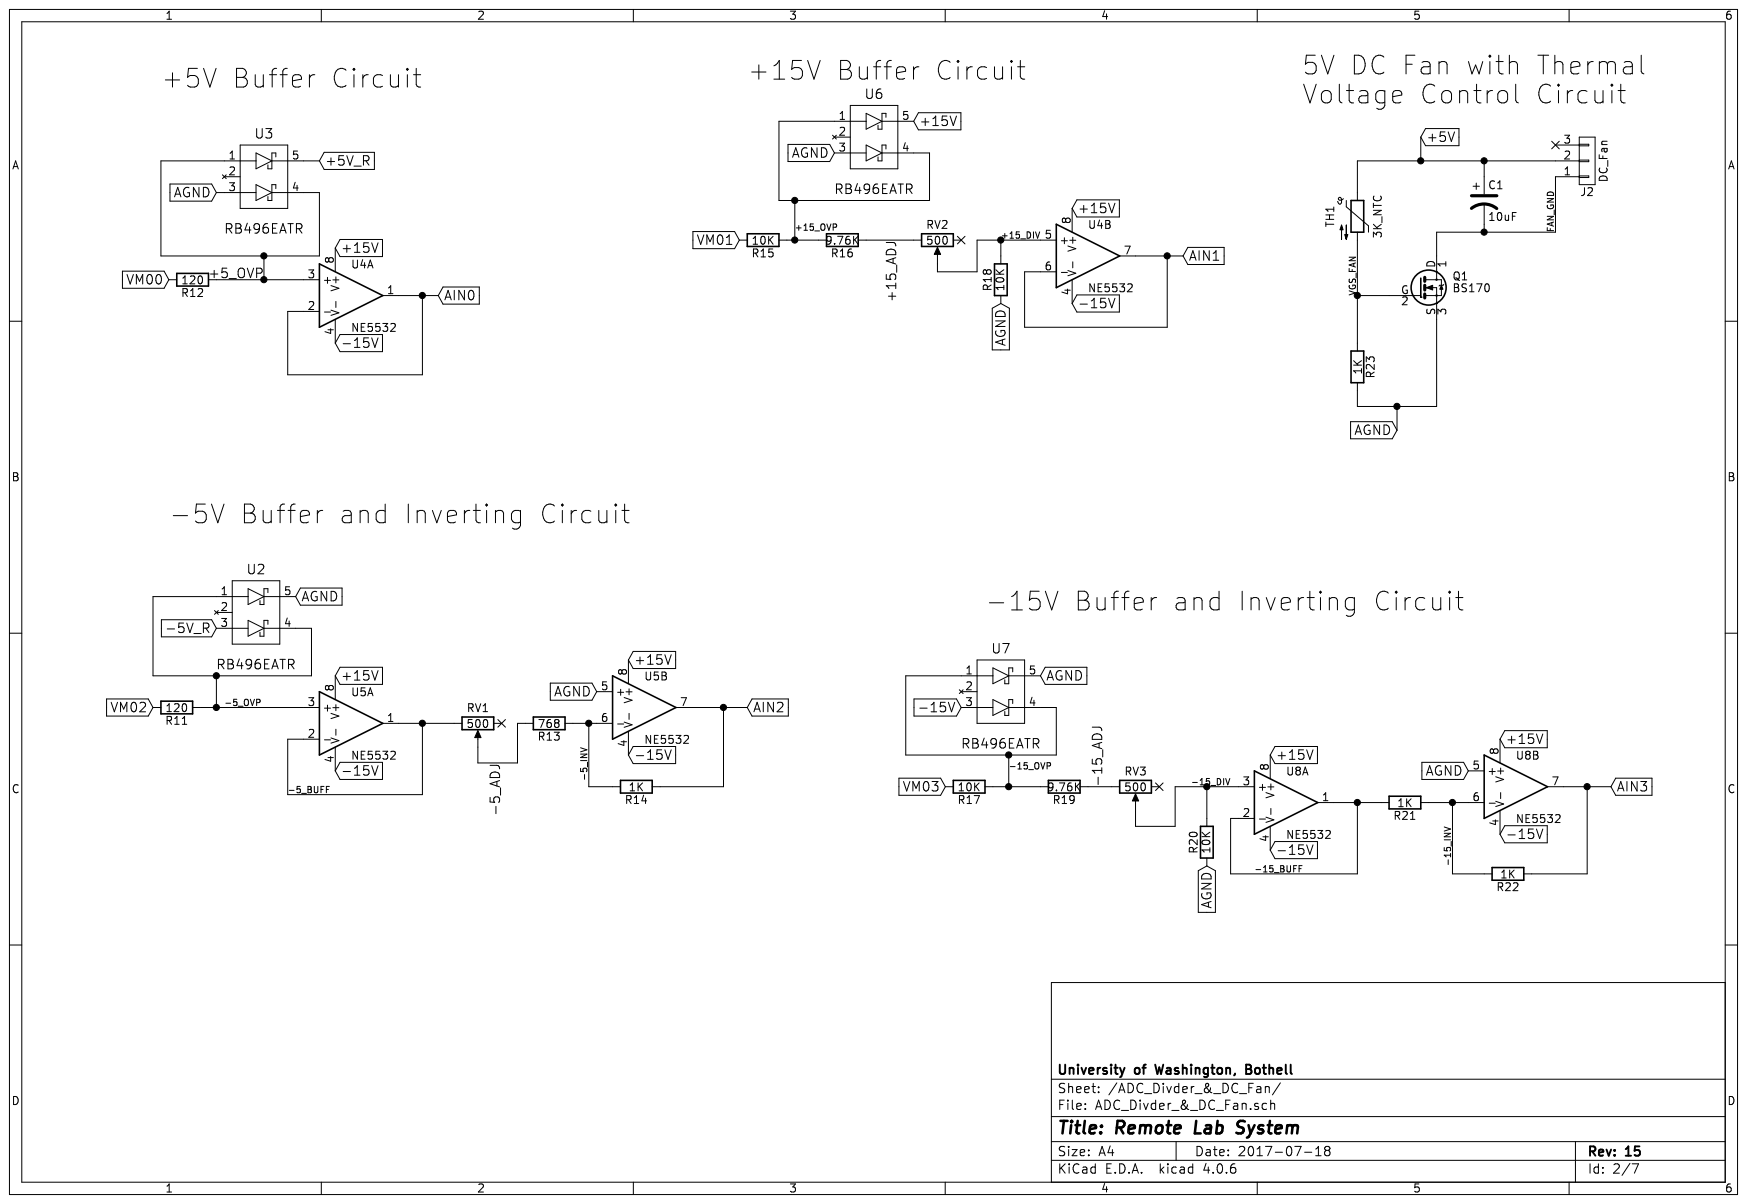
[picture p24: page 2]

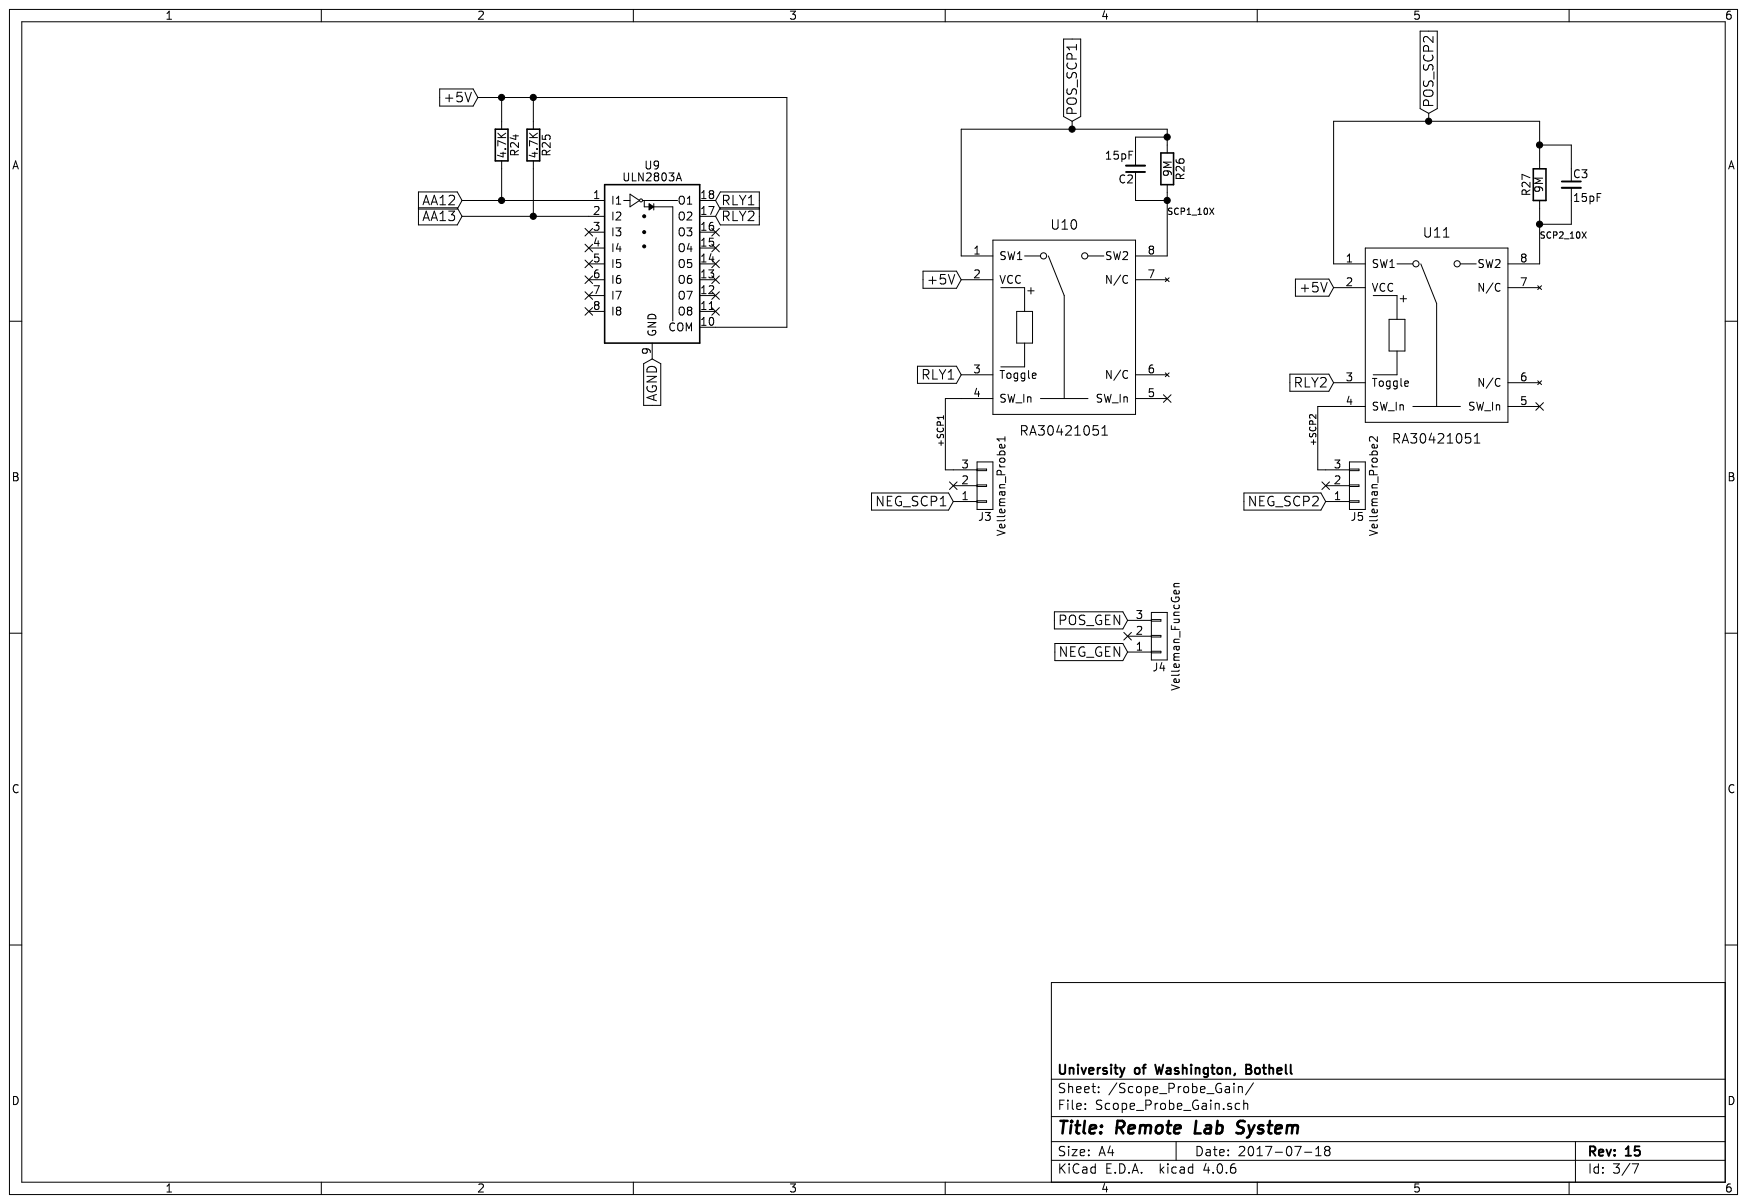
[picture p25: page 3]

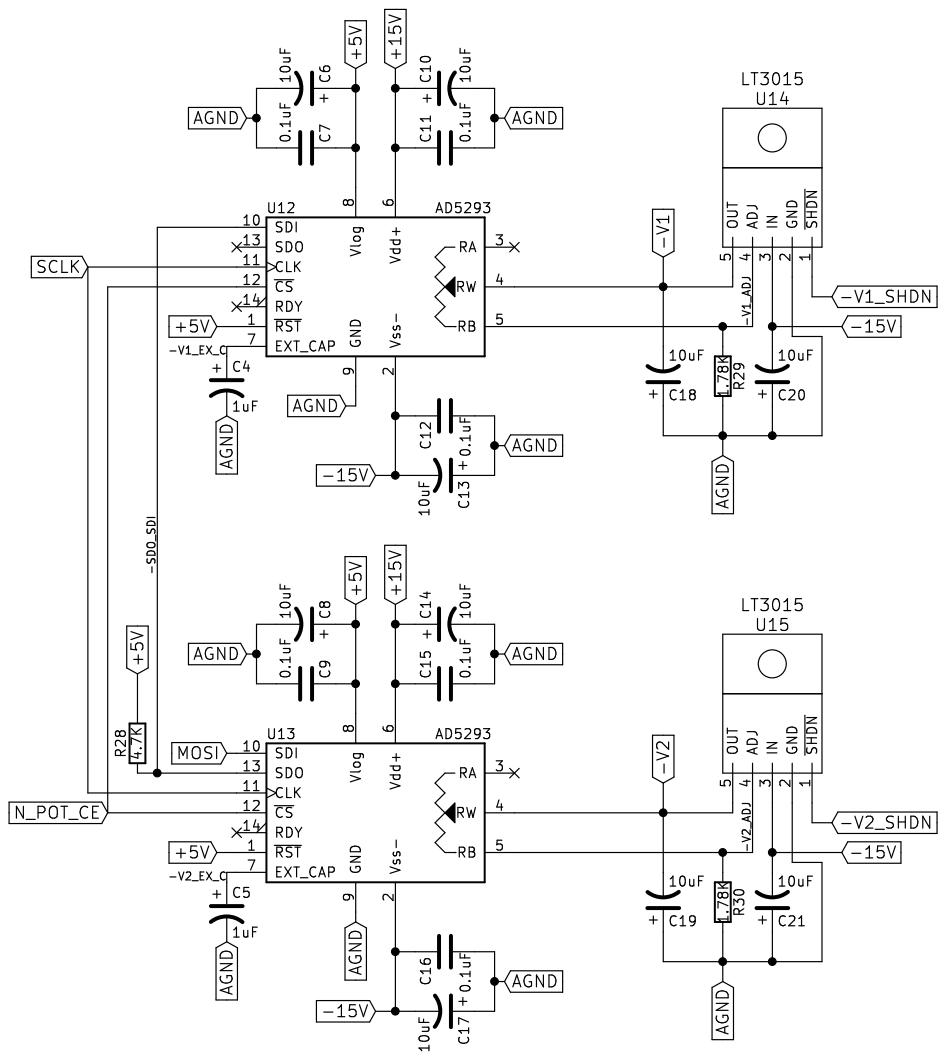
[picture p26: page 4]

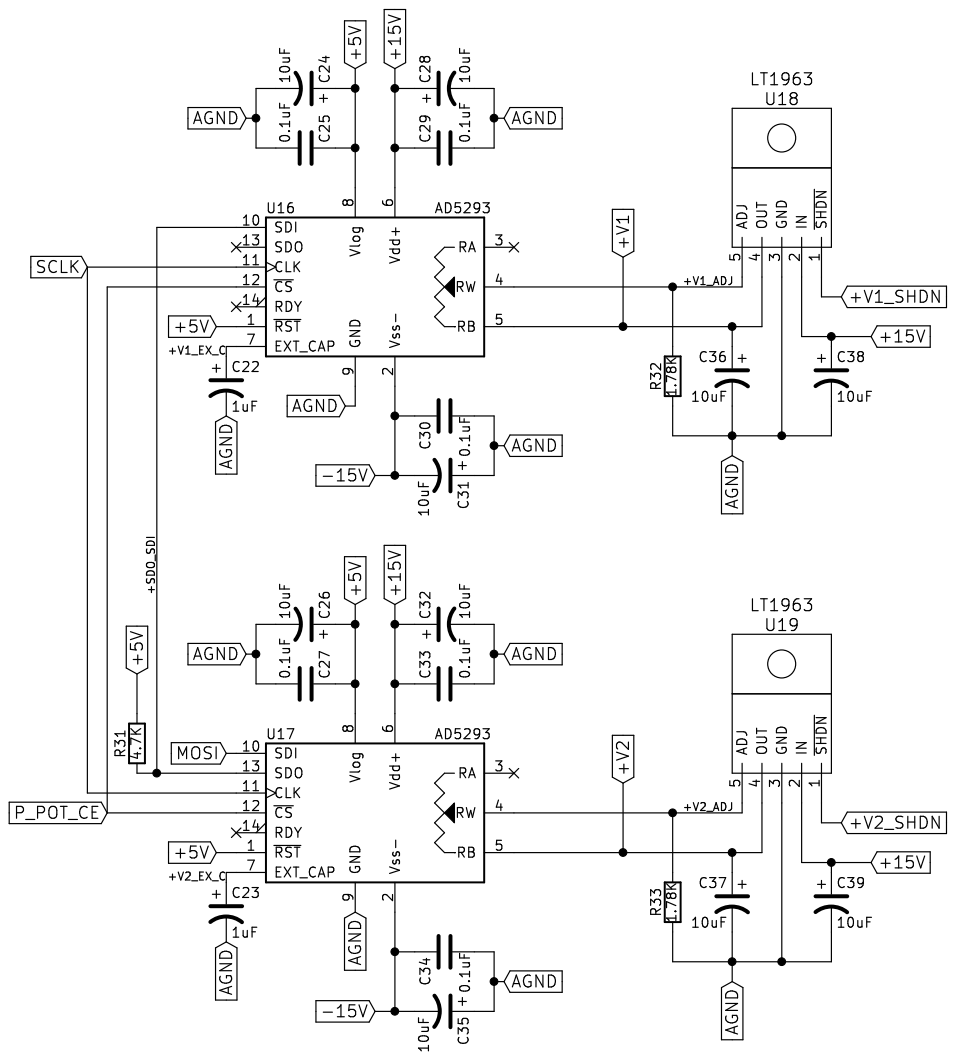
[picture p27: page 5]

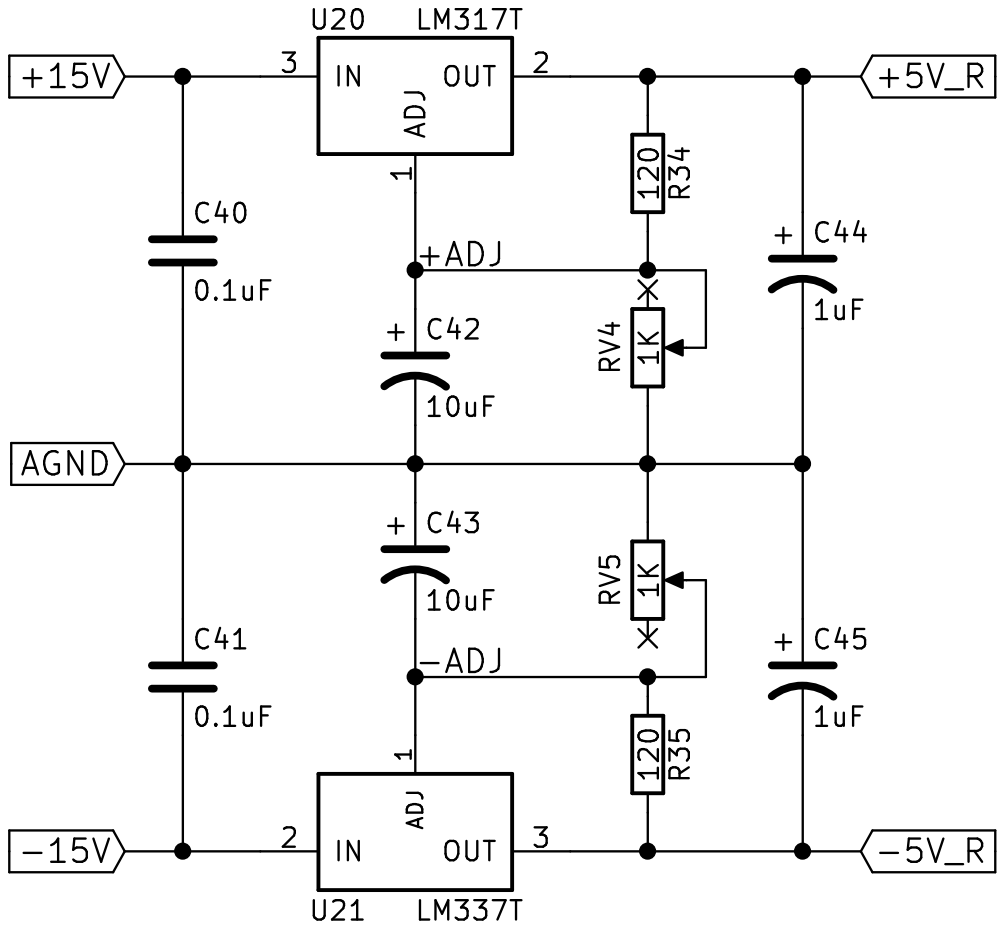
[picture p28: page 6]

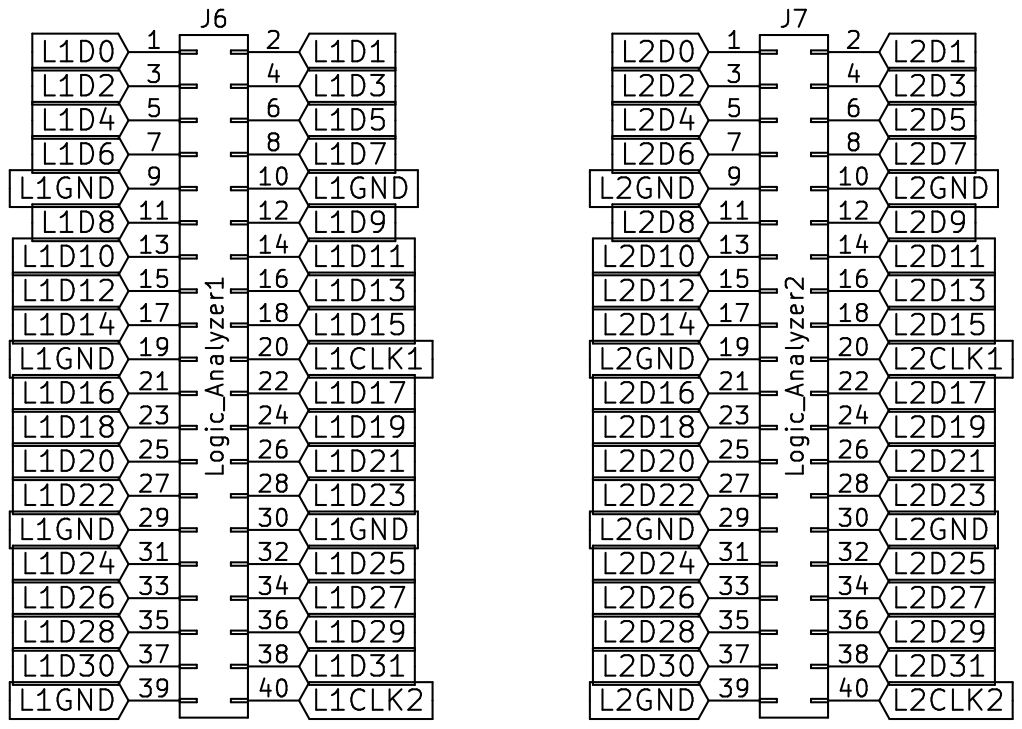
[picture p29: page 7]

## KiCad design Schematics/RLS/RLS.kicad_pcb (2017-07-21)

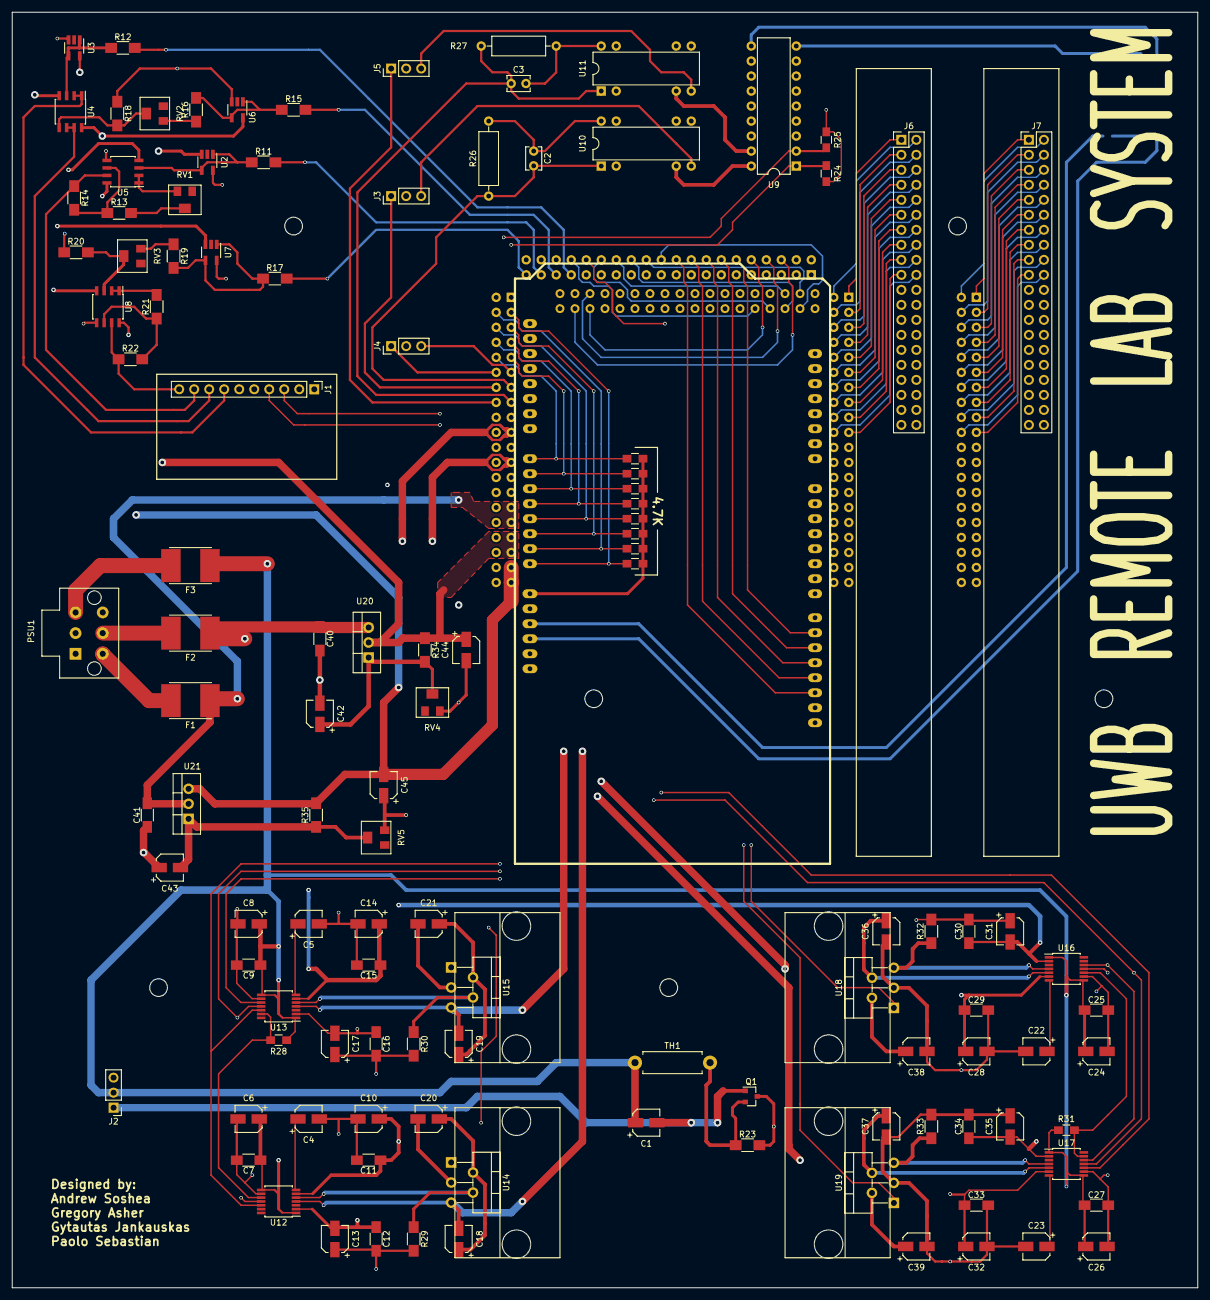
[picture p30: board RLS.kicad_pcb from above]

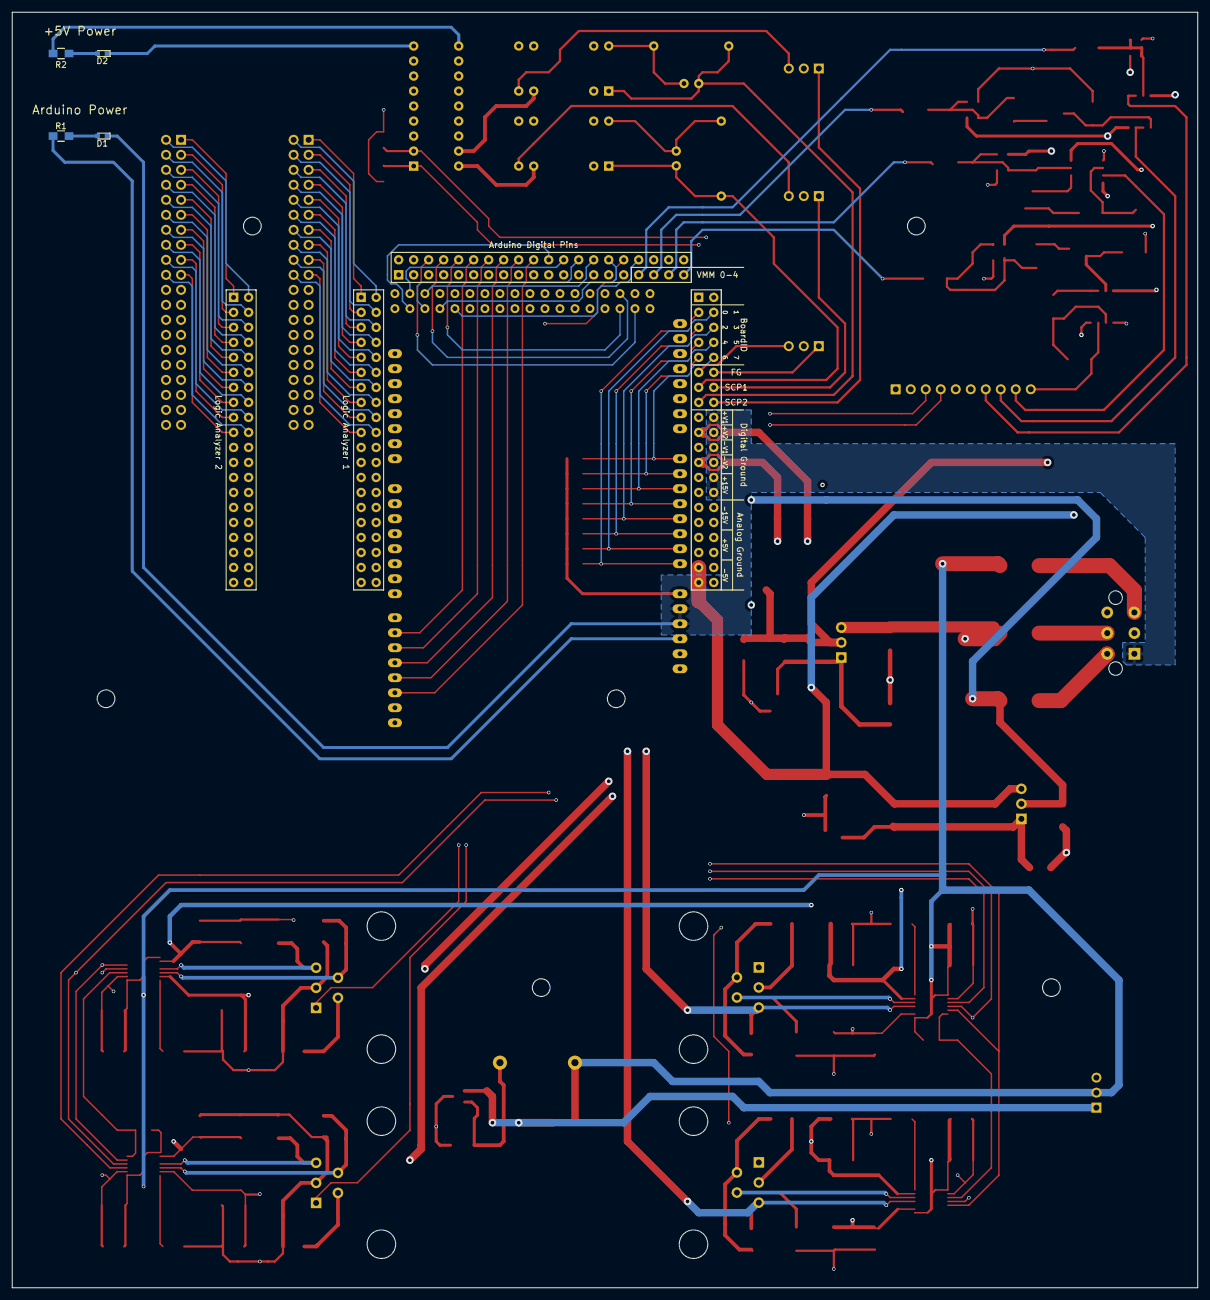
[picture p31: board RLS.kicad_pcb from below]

Board: 4 copper layers, 200.7 x 215.9 mm, 122 parts (4 on the bottom side), 188 nets.

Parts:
C1, C6, C8, C10, C13, C14, C17, C18, C19, C20, C21, C24, C26, C28, C31, C32, C35, C36, C37, C38, C39, C42, C43: 10uF; CP_Elec_4x5.3
C2, C3: 15pF; C_Disc_D3.8mm_W2.6mm_P2.50mm
C4, C5, C22, C23, C44, C45: 1uF; CP_Elec_4x5.3
C7, C9, C11, C12, C15, C16, C25, C27, C29, C30, C33, C34, C40, C41: 0.1uF; C_1206_HandSoldering
D1: AD_LED; LED_0603
D2: +5V_LED; LED_0603
DB1: DaughterBoard_Connectors; Daughterboard_4_Conn
F1: 1A; Fuse_SMD_Custom
F2: 1.5A; Fuse_SMD_Custom
F3: 4A; Fuse_SMD_Custom
J1: ADS1115; Pin_Header_Straight_1x10_Pitch2.54mm
J2: DC_Fan; Pin_Header_Straight_1x03_Pitch2.54mm
J3: Velleman_Probe1; Pin_Header_Straight_1x03_Pitch2.54mm
J4: Velleman_FuncGen; Pin_Header_Straight_1x03_Pitch2.54mm
J5: Velleman_Probe2; Pin_Header_Straight_1x03_Pitch2.54mm
J6: Logic_Analyzer1; Pin_Header_Straight_2x20_Pitch2.54mm
J7: Logic_Analyzer2; Pin_Header_Straight_2x20_Pitch2.54mm
PSU1: DIN_5; Molex_2x3_3.5mm
Q1: BS170; SOT-23
R1, R2, R3, R4, R5, R6, R7, R8, R9, R10, R24, R25, R28, R31: 4.7K; R_0805_HandSoldering
R11, R12, R34, R35: 120; R_1206_HandSoldering
R13: 768; R_1206_HandSoldering
R14, R21, R22, R23: 1K; R_1206_HandSoldering
R15, R17, R18, R20: 10K; R_1206_HandSoldering
R16, R19: 9.76K; R_1206_HandSoldering
R26, R27: 9M; R_Axial_DIN0309_L9.0mm_D3.2mm_P12.70mm_Horizontal
R29, R30, R32, R33: 1.78K; R_1206_HandSoldering
RV1, RV2, RV3: 500; Potentiometer_Trimmer_Bourns_PVG5A
RV4, RV5: 1K; Potentiometer_Trimmer_Bourns_PVG5A
TH1: 3K_NTC; R_Axial_DIN0411_L9.9mm_D3.6mm_P12.70mm_Horizontal
U1: ARDUINO_MEGA_SHIELD
U2, U3, U6, U7: RB496EATR; SOT-23-5_HandSoldering
U4, U5, U8: NE5532; SOIC-8_3.9x4.9mm_Pitch1.27mm
U9: ULN2803A; DIP-18_W7.62mm
U10, U11: RA30421051; DIP-8(14)_W7.62mm
U12, U13, U16, U17: AD5293; TSSOP-14_4.4x5mm_Pitch0.65mm
U14, U15: LT3015; TO-220-5_Vertical_Type1_w_Heatsink
U18, U19: LT1963; TO-220-5_Vertical_Type1_w_Heatsink
U20: LM317T; TO-220_Vertical
U21: LM337T; TO-220_Vertical

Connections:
+5V: C1.1, C6.1, C7.1, C8.1, C9.1, C24.1, C25.1, C26.1, C27.1, F3.1, J1.1, J2.2, R2.1, R3.2, R4.2, R5.2, R6.2, R7.2, R8.2, R9.2, R10.2, R24.1, R25.1, R28.2, R31.2, TH1.1, U1.V_IN, U9.10, U10.2, U11.2, U12.1, U12.8, U13.1, U13.8, U16.1, U16.8, U17.1, U17.8
+5V_R: C44.1, DB1.33, DB1.35, R34.1, U3.5, U20.2
+15V: C10.1, C11.1, C14.1, C15.1, C28.1, C29.1, C32.1, C33.1, C38.1, C39.1, C40.1, DB1.25, DB1.27, F2.1, U4.8, U5.8, U6.5, U8.8, U12.6, U13.6, U16.6, U17.6, U18.2, U19.2, U20.3
+V1: C36.1, DB1.17, U16.5, U18.4
+V1_SHDN: U1.AD9, U18.1
+V2: C37.1, DB1.19, U17.5, U19.4
+V2_SHDN: U1.AD8, U19.1
-5V_R: C45.2, DB1.37, DB1.39, R35.2, U2.3, U21.3
-15V: C12.1, C13.2, C16.1, C17.2, C20.2, C21.2, C30.1, C31.2, C34.1, C35.2, C41.2, DB1.29, DB1.31, F1.1, U4.4, U5.4, U7.3, U8.4, U12.2, U13.2, U14.3, U15.3, U16.2, U17.2, U21.2
-V1: C18.2, DB1.21, U12.4, U14.5
-V1_SHDN: U1.AD11, U14.1
-V2: C19.2, DB1.23, U13.4, U15.5
-V2_SHDN: U1.AD10, U15.1
/+5V_-5V_Regulators/+ADJ: C42.1, R34.2, RV4.2, U20.1
/+5V_-5V_Regulators/-ADJ: C43.2, R35.1, RV5.2, U21.1
/ADC_Divder_&_DC_Fan/+5_OVP: R12.1, U3.1, U3.4, U4.3
/ADC_Divder_&_DC_Fan/+15_ADJ: R16.1, RV2.1
/ADC_Divder_&_DC_Fan/+15_DIV: R18.2, RV2.2, U4.5
/ADC_Divder_&_DC_Fan/+15_OVP: R15.1, R16.2, U6.1, U6.4
/ADC_Divder_&_DC_Fan/-5_ADJ: R13.2, RV1.2
/ADC_Divder_&_DC_Fan/-5_BUFF: RV1.3, U5.1, U5.2
/ADC_Divder_&_DC_Fan/-5_INV: R13.1, R14.2, U5.6
/ADC_Divder_&_DC_Fan/-5_OVP: R11.1, U2.1, U2.4, U5.3
/ADC_Divder_&_DC_Fan/-15_ADJ: R19.1, RV3.3
/ADC_Divder_&_DC_Fan/-15_BUFF: R21.2, U8.1, U8.2
/ADC_Divder_&_DC_Fan/-15_DIV: R20.2, RV3.2, U8.3
/ADC_Divder_&_DC_Fan/-15_INV: R21.1, R22.2, U8.6
/ADC_Divder_&_DC_Fan/-15_OVP: R17.1, R19.2, U7.1, U7.4
/ADC_Divder_&_DC_Fan/FAN_GND: C1.2, J2.1, Q1.1
/ADC_Divder_&_DC_Fan/VGS_FAN: Q1.2, R23.1, TH1.2
/ARD_LED: D1.2, R1.2
/BID0: DB1.3, R3.1, U1.AD0
/BID1: DB1.4, R7.1, U1.AD1
/BID2: DB1.5, R4.1, U1.AD2
/BID3: DB1.6, R8.1, U1.AD3
/BID4: DB1.7, R5.1, U1.AD4
/BID5: DB1.8, R9.1, U1.AD5
/BID6: DB1.9, R6.1, U1.AD6
/BID7: DB1.10, R10.1, U1.AD7
/DIN5: F3.2, PSU1.3
/DIN+15: F2.2, PSU1.5
/DIN-15: F1.2, PSU1.4
/Negative_Regulators/-SDO_SDI: R28.1, U12.10, U13.13
/Negative_Regulators/-V1_ADJ: R29.1, U12.5, U14.4
/Negative_Regulators/-V1_EX_C: C4.1, U12.7
/Negative_Regulators/-V2_ADJ: R30.1, U13.5, U15.4
/Negative_Regulators/-V2_EX_C: C5.1, U13.7
/PSU_LED: D2.2, R2.2
/Positive_Regulators/+SDO_SDI: R31.1, U16.10, U17.13
/Positive_Regulators/+V1_ADJ: R32.1, U16.4, U18.5
/Positive_Regulators/+V1_EX_C: C22.1, U16.7
/Positive_Regulators/+V2_ADJ: R33.1, U17.4, U19.5
/Positive_Regulators/+V2_EX_C: C23.1, U17.7
/Scope_Probe_Gain/+SCP1: J3.3, U10.4
/Scope_Probe_Gain/+SCP2: J5.3, U11.4
/Scope_Probe_Gain/SCP1_10X: C2.1, R26.2, U10.8
/Scope_Probe_Gain/SCP2_10X: C3.2, R27.1, U11.8
AA12: R24.2, U1.AD12, U9.1
AA13: R25.2, U1.AD13, U9.2
AA14: DB1.2, U1.AD14
AA15: DB1.1, U1.AD15
AD9: DB1.52, U1.9
AD10: DB1.54, U1.10
AD11: DB1.56, U1.11
AD12: DB1.58, U1.12
AD13: DB1.60, U1.13
AD22: DB1.62, U1.22
AD23: DB1.64, U1.23
AD24: DB1.66, U1.24
AD25: DB1.68, U1.25
AD26: DB1.70, U1.26
AD27: DB1.72, U1.27
AD28: DB1.74, U1.28
AD29: DB1.76, U1.29
AD30: DB1.78, U1.30
AD31: DB1.80, U1.31
AD32: DB1.41, U1.32
AD33: DB1.43, U1.33
AD34: DB1.45, U1.34
AD35: DB1.47, U1.35
AD36: DB1.49, U1.36
AD37: DB1.51, U1.37
AD38: DB1.53, U1.38
AD39: DB1.55, U1.39
AD40: DB1.57, U1.40
AD41: DB1.59, U1.41
AD42: DB1.61, U1.42
AD43: DB1.63, U1.43
AD44: DB1.65, U1.44
AD45: DB1.67, U1.45
AD46: DB1.69, U1.46
AD47: DB1.71, U1.47
AD_LED: R1.1, U1.5V
AGND: C4.2, C5.2, C6.2, C7.2, C8.2, C9.2, C10.2, C11.2, C12.2, C13.1, C14.2, C15.2, C16.2, C17.1, C18.1, C19.1, C20.1, C21.1, C22.2, C23.2, C24.2, C25.2, C26.2, C27.2, C28.2, C29.2, C30.2, C31.1, C32.2, C33.2, C34.2, C35.1, C36.2, C37.2, C38.2, C39.2, C40.2, C41.1, C42.2, C43.1, C44.2, C45.1, D2.1, DB1.30, DB1.32, DB1.34, DB1.36, DB1.38, DB1.40, J1.2, J1.5, PSU1.2, Q1.3, R18.1, R20.1, R23.2, R29.2, R30.2, R32.2, R33.2, RV4.3, RV5.3, U2.5, U3.3, U5.5, U6.3, U7.5, U8.5, U9.9, U12.9, U13.9, U14.2, U15.2, U16.9, U17.9, U18.3, U19.3
AIN0: J1.7, U4.1, U4.2
AIN1: J1.8, U4.6, U4.7
AIN2: J1.9, R14.1, U5.7
AIN3: J1.10, R22.1, U8.7
DGND: D1.1, DB1.18, DB1.20, DB1.22, DB1.24, DB1.26, DB1.28, PSU1.1, U1.GND1, U1.GND2
L1CLK1: DB1.100, J6.20
L1CLK2: DB1.120, J6.40
L1D0: DB1.81, J6.1
L1D1: DB1.82, J6.2
L1D2: DB1.83, J6.3
L1D3: DB1.84, J6.4
L1D4: DB1.85, J6.5
L1D5: DB1.86, J6.6
L1D6: DB1.87, J6.7
L1D7: DB1.88, J6.8
L1D8: DB1.91, J6.11
L1D9: DB1.92, J6.12
L1D10: DB1.93, J6.13
L1D11: DB1.94, J6.14
L1D12: DB1.95, J6.15
L1D13: DB1.96, J6.16
L1D14: DB1.97, J6.17
L1D15: DB1.98, J6.18
L1D16: DB1.101, J6.21
L1D17: DB1.102, J6.22
L1D18: DB1.103, J6.23
L1D19: DB1.104, J6.24
L1D20: DB1.105, J6.25
L1D21: DB1.106, J6.26
L1D22: DB1.107, J6.27
L1D23: DB1.108, J6.28
L1D24: DB1.111, J6.31
L1D25: DB1.112, J6.32
L1D26: DB1.113, J6.33
L1D27: DB1.114, J6.34
L1D28: DB1.115, J6.35
L1D29: DB1.116, J6.36
L1D30: DB1.117, J6.37
L1D31: DB1.118, J6.38
L1GND: DB1.89, DB1.90, DB1.99, DB1.109, DB1.110, DB1.119, J6.9, J6.10, J6.19, J6.29, J6.30, J6.39
L2CLK1: DB1.140, J7.20
L2CLK2: DB1.160, J7.40
L2D0: DB1.121, J7.1
L2D1: DB1.122, J7.2
L2D2: DB1.123, J7.3
L2D3: DB1.124, J7.4
L2D4: DB1.125, J7.5
L2D5: DB1.126, J7.6
L2D6: DB1.127, J7.7
L2D7: DB1.128, J7.8
L2D8: DB1.131, J7.11
L2D9: DB1.132, J7.12
L2D10: DB1.133, J7.13
L2D11: DB1.134, J7.14
L2D12: DB1.135, J7.15
L2D13: DB1.136, J7.16
L2D14: DB1.137, J7.17
L2D15: DB1.138, J7.18
L2D16: DB1.141, J7.21
L2D17: DB1.142, J7.22
L2D18: DB1.143, J7.23
L2D19: DB1.144, J7.24
L2D20: DB1.145, J7.25
L2D21: DB1.146, J7.26
L2D22: DB1.147, J7.27
L2D23: DB1.148, J7.28
L2D24: DB1.151, J7.31
L2D25: DB1.152, J7.32
L2D26: DB1.153, J7.33
L2D27: DB1.154, J7.34
L2D28: DB1.155, J7.35
L2D29: DB1.156, J7.36
L2D30: DB1.157, J7.37
L2D31: DB1.158, J7.38
L2GND: DB1.129, DB1.130, DB1.139, DB1.149, DB1.150, DB1.159, J7.9, J7.10, J7.19, J7.29, J7.30, J7.39
MISO: DB1.50, U1.50
MOSI: DB1.48, U1.51, U13.10, U17.10
NEG_GEN: DB1.12, J4.1
NEG_SCP1: DB1.14, J3.1
NEG_SCP2: DB1.16, J5.1
N_POT_CE: U1.53, U12.12, U13.12
POS_GEN: DB1.11, J4.3
POS_SCP1: C2.2, DB1.13, R26.1, U10.1
POS_SCP2: C3.1, DB1.15, R27.2, U11.1
P_POT_CE: U1.48, U16.12, U17.12
RLY1: U9.18, U10.3
RLY2: U9.17, U11.3
SCL: DB1.42, J1.3, U1.21
SCLK: DB1.46, U1.52, U12.11, U13.11, U16.11, U17.11
SDA: DB1.44, J1.4, U1.20
VM00: DB1.73, R12.2
VM01: DB1.75, R15.2
VM02: DB1.77, R11.2
VM03: DB1.79, R17.2

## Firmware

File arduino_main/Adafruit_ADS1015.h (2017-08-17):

/**************************************************************************/
/*!
    @file     Adafruit_ADS1015.h
    @author   K. Townsend (Adafruit Industries)
    @license  BSD (see license.txt)

    This is a library for the Adafruit ADS1015 breakout board
    ----> https://www.adafruit.com/products/???

    Adafruit invests time and resources providing this open source code,
    please support Adafruit and open-source hardware by purchasing
    products from Adafruit!

    @section  HISTORY

    v1.0  - First release
    v1.1  - Added ADS1115 support - W. Earl
*/
/**************************************************************************/

#if ARDUINO >= 100
 #include "Arduino.h"
#else
 #include "WProgram.h"
#endif

#include <Wire.h>
/*=========================================================================
    I2C ADDRESS/BITS
    -----------------------------------------------------------------------*/
    #define ADS1015_ADDRESS                 (0x48)    // 1001 000 (ADDR = GND)
/*=========================================================================*/

/*=========================================================================
    CONVERSION DELAY (in mS)
    -----------------------------------------------------------------------*/
    #define ADS1015_CONVERSIONDELAY         (1)
    #define ADS1115_CONVERSIONDELAY         (8)
/*=========================================================================*/

/*=========================================================================
    POINTER REGISTER
    -----------------------------------------------------------------------*/
    #define ADS1015_REG_POINTER_MASK        (0x03)
    #define ADS1015_REG_POINTER_CONVERT     (0x00)
    #define ADS1015_REG_POINTER_CONFIG      (0x01)
    #define ADS1015_REG_POINTER_LOWTHRESH   (0x02)
    #define ADS1015_REG_POINTER_HITHRESH    (0x03)
/*=========================================================================*/

/*=========================================================================
    CONFIG REGISTER
    -----------------------------------------------------------------------*/
    #define ADS1015_REG_CONFIG_OS_MASK      (0x8000)
    #define ADS1015_REG_CONFIG_OS_SINGLE    (0x8000)  // Write: Set to start a single-conversion
    #define ADS1015_REG_CONFIG_OS_BUSY      (0x0000)  // Read: Bit = 0 when conversion is in progress
    #define ADS1015_REG_CONFIG_OS_NOTBUSY   (0x8000)  // Read: Bit = 1 when device is not performing a conversion

    #define ADS1015_REG_CONFIG_MUX_MASK     (0x7000)
    #define ADS1015_REG_CONFIG_MUX_DIFF_0_1 (0x0000)  // Differential P = AIN0, N = AIN1 (default)
    #define ADS1015_REG_CONFIG_MUX_DIFF_0_3 (0x1000)  // Differential P = AIN0, N = AIN3
    #define ADS1015_REG_CONFIG_MUX_DIFF_1_3 (0x2000)  // Differential P = AIN1, N = AIN3
    #define ADS1015_REG_CONFIG_MUX_DIFF_2_3 (0x3000)  // Differential P = AIN2, N = AIN3
    #define ADS1015_REG_CONFIG_MUX_SINGLE_0 (0x4000)  // Single-ended AIN0
    #define ADS1015_REG_CONFIG_MUX_SINGLE_1 (0x5000)  // Single-ended AIN1
    #define ADS1015_REG_CONFIG_MUX_SINGLE_2 (0x6000)  // Single-ended AIN2
    #define ADS1015_REG_CONFIG_MUX_SINGLE_3 (0x7000)  // Single-ended AIN3

    #define ADS1015_REG_CONFIG_PGA_MASK     (0x0E00)
    #define ADS1015_REG_CONFIG_PGA_6_144V   (0x0000)  // +/-6.144V range = Gain 2/3
    #define ADS1015_REG_CONFIG_PGA_4_096V   (0x0200)  // +/-4.096V range = Gain 1
    #define ADS1015_REG_CONFIG_PGA_2_048V   (0x0400)  // +/-2.048V range = Gain 2 (default)
    #define ADS1015_REG_CONFIG_PGA_1_024V   (0x0600)  // +/-1.024V range = Gain 4
    #define ADS1015_REG_CONFIG_PGA_0_512V   (0x0800)  // +/-0.512V range = Gain 8
    #define ADS1015_REG_CONFIG_PGA_0_256V   (0x0A00)  // +/-0.256V range = Gain 16

    #define ADS1015_REG_CONFIG_MODE_MASK    (0x0100)
    #define ADS1015_REG_CONFIG_MODE_CONTIN  (0x0000)  // Continuous conversion mode
    #define ADS1015_REG_CONFIG_MODE_SINGLE  (0x0100)  // Power-down single-shot mode (default)

    #define ADS1015_REG_CONFIG_DR_MASK      (0x00E0)  
    #define ADS1015_REG_CONFIG_DR_128SPS    (0x0000)  // 128 samples per second
    #define ADS1015_REG_CONFIG_DR_250SPS    (0x0020)  // 250 samples per second
    #define ADS1015_REG_CONFIG_DR_490SPS    (0x0040)  // 490 samples per second
    #define ADS1015_REG_CONFIG_DR_920SPS    (0x0060)  // 920 samples per second
    #define ADS1015_REG_CONFIG_DR_1600SPS   (0x0080)  // 1600 samples per second (default)
    #define ADS1015_REG_CONFIG_DR_2400SPS   (0x00A0)  // 2400 samples per second
    #define ADS1015_REG_CONFIG_DR_3300SPS   (0x00C0)  // 3300 samples per second

    #define ADS1015_REG_CONFIG_CMODE_MASK   (0x0010)
    #define ADS1015_REG_CONFIG_CMODE_TRAD   (0x0000)  // Traditional comparator with hysteresis (default)
    #define ADS1015_REG_CONFIG_CMODE_WINDOW (0x0010)  // Window comparator

    #define ADS1015_REG_CONFIG_CPOL_MASK    (0x0008)
    #define ADS1015_REG_CONFIG_CPOL_ACTVLOW (0x0000)  // ALERT/RDY pin is low when active (default)
    #define ADS1015_REG_CONFIG_CPOL_ACTVHI  (0x0008)  // ALERT/RDY pin is high when active

    #define ADS1015_REG_CONFIG_CLAT_MASK    (0x0004)  // Determines if ALERT/RDY pin latches once asserted
    #define ADS1015_REG_CONFIG_CLAT_NONLAT  (0x0000)  // Non-latching comparator (default)
    #define ADS1015_REG_CONFIG_CLAT_LATCH   (0x0004)  // Latching comparator

    #define ADS1015_REG_CONFIG_CQUE_MASK    (0x0003)
    #define ADS1015_REG_CONFIG_CQUE_1CONV   (0x0000)  // Assert ALERT/RDY after one conversions
    #define ADS1015_REG_CONFIG_CQUE_2CONV   (0x0001)  // Assert ALERT/RDY after two conversions
    #define ADS1015_REG_CONFIG_CQUE_4CONV   (0x0002)  // Assert ALERT/RDY after four conversions
    #define ADS1015_REG_CONFIG_CQUE_NONE    (0x0003)  // Disable the comparator and put ALERT/RDY in high state (default)
/*=========================================================================*/

typedef enum
{
  GAIN_TWOTHIRDS    = ADS1015_REG_CONFIG_PGA_6_144V,
  GAIN_ONE          = ADS1015_REG_CONFIG_PGA_4_096V,
  GAIN_TWO          = ADS1015_REG_CONFIG_PGA_2_048V,
  GAIN_FOUR         = ADS1015_REG_CONFIG_PGA_1_024V,
  GAIN_EIGHT        = ADS1015_REG_CONFIG_PGA_0_512V,
  GAIN_SIXTEEN      = ADS1015_REG_CONFIG_PGA_0_256V
} adsGain_t;

class Adafruit_ADS1015
{
protected:
   // Instance-specific properties
   uint8_t   m_i2cAddress;
   uint8_t   m_conversionDelay;
   uint8_t   m_bitShift;
   adsGain_t m_gain;

 public:
  Adafruit_ADS1015(uint8_t i2cAddress = ADS1015_ADDRESS);
  void begin(void);
  uint16_t  readADC_SingleEnded(uint8_t channel);
  int16_t   readADC_Differential_0_1(void);
  int16_t   readADC_Differential_2_3(void);
  void      startComparator_SingleEnded(uint8_t channel, int16_t threshold);
  int16_t   getLastConversionResults();
  void      setGain(adsGain_t gain);
  adsGain_t getGain(void);
  double getCh0();
  double getCh1();
  double getCh2();
  double getCh3();

 private:
};

// Derive from ADS1105 & override construction to set properties
class Adafruit_ADS1115 : public Adafruit_ADS1015
{
 public:
  Adafruit_ADS1115(uint8_t i2cAddress = ADS1015_ADDRESS);

 private:
};

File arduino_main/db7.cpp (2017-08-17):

/******************************************************************************
	db7.cpp
	This implementation file contains code for Daugherboard 7,
	part of the Remote Lab System at the University of
	Washington Bothell. See db7.h.
	This code is designed to run on an Arduino Mega 2560.
	
	Created by Ellery Walsh, April 2016
	Reseased into the public domain.
******************************************************************************/

#include "Arduino.h"
#include "db7.h"

//set up connections between arduino and switches, and arduino and dffs
  const int switchU1_In1_In2 = 22; // Connect or bypass XOR7
  const int switchU1_In3_In4 = 23; // Connect or bypass XOR6
  
  const int switchU2_In1_In2 = 24; // Connect or bypass XOR5
  const int switchU2_In3_In4 = 25; // Connect or bypass XOR4
  
  const int switchU3_In1_In2 = 30; // Connect or bypass XOR3
  const int switchU3_In3_In4 = 31; // Connect or bypass XOR2
  
  const int switchU4_In1_In2 = 32; // Connect or bypass XOR1
  
  const int dff1Preset = 36; // Preset 2 on DFF4
  const int dff2Preset = 35; // Preset 1 on DFF4
  const int dff3Preset = 34; // Preset 2 on DFF3
  const int dff4Preset = 33; // Preset 1 on DFF3
  const int dff5Preset = 29; // Preset 2 on DFF2
  const int dff6Preset = 28; // Preset 1 on DFF2
  const int dff7Preset = 27; // Preset 2 on DFF1
  const int dff8Preset = 26; // Preset 1 on DFF1
	
  const int clearAllPresets = 39; // used to reset all flipflop presets to 0
  
  const int connectClock = 37; // determines whether clock signal is connected to all dffs

// set up variables used for parsing input from user interface
  bool XOR1Connected = 0;
  bool XOR2Connected = 0;
  bool XOR3Connected = 0;
  bool XOR4Connected = 0;
  bool XOR5Connected = 0;
  bool XOR6Connected = 0;
  bool XOR7Connected = 0;
  
  bool dff1PresetState = 0;
  bool dff2PresetState = 0;
  bool dff3PresetState = 0;
  bool dff4PresetState = 0;
  bool dff5PresetState = 0;
  bool dff6PresetState = 0;
  bool dff7PresetState = 0;
  bool dff8PresetState = 0;
  
  bool clearState = 0;

void DB7::configurePins() {
  pinMode(switchU1_In1_In2, OUTPUT);
  pinMode(switchU1_In3_In4, OUTPUT);
  
  pinMode(switchU2_In1_In2, OUTPUT);
  pinMode(switchU2_In3_In4, OUTPUT);

  pinMode(switchU3_In1_In2, OUTPUT);
  pinMode(switchU3_In3_In4, OUTPUT);
  
  pinMode(switchU4_In1_In2, OUTPUT);
  
  pinMode(dff1Preset, OUTPUT);
  pinMode(dff2Preset, OUTPUT);
  pinMode(dff3Preset, OUTPUT);
  pinMode(dff4Preset, OUTPUT);
  pinMode(dff5Preset, OUTPUT);
  pinMode(dff6Preset, OUTPUT);
  pinMode(dff7Preset, OUTPUT);
  pinMode(dff8Preset, OUTPUT);
  
  pinMode(clearAllPresets, OUTPUT);
  
  pinMode(connectClock, OUTPUT); // determines whether clock signal is connected to all dffs
  
  // Disconnect clock from circuit
  digitalWrite(connectClock, 0);
  
  // clear all dffs
  digitalWrite(clearAllPresets, HIGH);
  digitalWrite(clearAllPresets, LOW);
  digitalWrite(clearAllPresets, HIGH);
  
  // set up all presets to zero
    digitalWrite(dff1Preset, HIGH);
	digitalWrite(dff2Preset, HIGH);
	digitalWrite(dff3Preset, HIGH);
	digitalWrite(dff4Preset, HIGH);
	digitalWrite(dff5Preset, HIGH);
	digitalWrite(dff6Preset, HIGH);
	digitalWrite(dff7Preset, HIGH);
	digitalWrite(dff8Preset, HIGH);
}

void DB7::execute(String Board_7_Serial) {
  // variables used for parsing input from interface
  // the default message is board_7,0,0,0,0,0,0,0,0,0,0,0,0,0,0,0,0,0
  // index                  01234567890123456789012345678901234567890
  XOR1Connected = Board_7_Serial.substring(8,9).toInt();
  XOR2Connected = Board_7_Serial.substring(10,11).toInt();
  XOR3Connected = Board_7_Serial.substring(12,13).toInt();
  XOR4Connected = Board_7_Serial.substring(14,15).toInt();
  XOR5Connected = Board_7_Serial.substring(16,17).toInt();
  XOR6Connected = Board_7_Serial.substring(18,19).toInt();
  XOR7Connected = Board_7_Serial.substring(20,21).toInt();
  
  dff1PresetState = Board_7_Serial.substring(22,23).toInt();
  dff2PresetState = Board_7_Serial.substring(24,25).toInt();
  dff3PresetState = Board_7_Serial.substring(26,27).toInt();
  dff4PresetState = Board_7_Serial.substring(28,29).toInt();
  dff5PresetState = Board_7_Serial.substring(30,31).toInt();
  dff6PresetState = Board_7_Serial.substring(32,33).toInt();
  dff7PresetState = Board_7_Serial.substring(34,35).toInt();
  dff8PresetState = Board_7_Serial.substring(36,37).toInt();
  
  clockConnectedState = Board_7_Serial.substring(38,39).toInt();
  
  clearState = Board_7_Serial.substring(40,41).toInt();
  
  //XOR connections
    // State of XOR1
  if (XOR1Connected == 0) { //XOR connected
	  digitalWrite(switchU4_In1_In2, HIGH);  
  }
  else if (XOR1Connected == 1) { //XOR bypassed
	  digitalWrite(switchU4_In1_In2, LOW);  
  }
  
      // State of XOR2
  if (XOR2Connected == 0) { //XOR connected
	  digitalWrite(switchU3_In3_In4, HIGH);  
  }
  else if (XOR2Connected == 1) { //XOR bypassed
	  digitalWrite(switchU3_In3_In4, LOW);  
  }
      // State of XOR3
  if (XOR3Connected == 0) { //XOR connected
	  digitalWrite(switchU3_In1_In2, HIGH);  
  }
  else if (XOR3Connected == 1) { //XOR bypassed
	  digitalWrite(switchU3_In1_In2, LOW);  
  }
      // State of XOR4
  if (XOR4Connected == 0) { //XOR connected
	  digitalWrite(switchU2_In3_In4, HIGH);  
  }
  else if (XOR4Connected == 1) { //XOR bypassed
	  digitalWrite(switchU2_In3_In4, LOW);  
  }
      // State of XOR5
  if (XOR5Connected == 0) { //XOR connected
	  digitalWrite(switchU2_In1_In2, HIGH);  
  }
  else if (XOR5Connected == 1) { //XOR bypassed
	  digitalWrite(switchU2_In1_In2, LOW);  
  }
      // State of XOR6
  if (XOR6Connected == 0) { //XOR connected
	  digitalWrite(switchU1_In3_In4, HIGH);  
  }
  else if (XOR6Connected == 1) { //XOR bypassed
	  digitalWrite(switchU1_In3_In4, LOW);  
  }
        // State of XOR7
  if (XOR7Connected == 0) { //XOR connected
	  digitalWrite(switchU1_In1_In2, HIGH);  
  }
  else if (XOR7Connected == 1) { //XOR bypassed
	  digitalWrite(switchU1_In1_In2, LOW);  
  }
  
  //dff presets
  // note: state of 0 means no signals have been sent, 
  // so no need to check for that case
      // State of dff1
  if (dff1PresetState == 1) { //dff preset to 1
	  digitalWrite(dff1Preset, LOW);
	  digitalWrite(dff1Preset, HIGH);
  }
  
        // State of dff2
  if (dff2PresetState == 1) { //dff preset to 1
	  digitalWrite(dff2Preset, LOW);
	  digitalWrite(dff2Preset, HIGH); 
  }
        // State of dff3
  if (dff3PresetState == 1) { //dff preset to 1
	  digitalWrite(dff3Preset, LOW);
	  digitalWrite(dff3Preset, HIGH);
  }
        // State of dff4
  if (dff4PresetState == 1) { //dff preset to 1
	  digitalWrite(dff4Preset, LOW);
	  digitalWrite(dff4Preset, HIGH);  
  }
        // State of dff5
  if (dff5PresetState == 1) { //dff preset to 1
	  digitalWrite(dff5Preset, LOW);
	  digitalWrite(dff5Preset, HIGH);
  }
        // State of dff6
  if (dff6PresetState == 1) { //dff preset to 1
	  digitalWrite(dff6Preset, LOW);
	  digitalWrite(dff6Preset, HIGH);
  }
        // State of dff7
  if (dff7PresetState == 1) { //dff preset to 1
	  digitalWrite(dff7Preset, LOW);
	  digitalWrite(dff7Preset, HIGH); 
  }
        // State of dff8
  if (dff8PresetState == 1) { //dff preset to 1
	  digitalWrite(dff8Preset, LOW);
	  digitalWrite(dff8Preset, HIGH);
  }
  
  // state of clock
  if (clockConnectedState == 0) { // clock disconnected
	  digitalWrite(connectClock, LOW);
  }
  else if (clockConnectedState == 1) { // clock connected
	  digitalWrite(connectClock, HIGH);
  }
  
  // state of clear button
  // if button is not pressed, a zero will be received
  // this means nothing needs to be done, so we don't need
  // to check for this case
  if (clearState == 1) {
	digitalWrite(clearAllPresets, HIGH);
    digitalWrite(clearAllPresets, LOW);
    digitalWrite(clearAllPresets, HIGH);
  }
  
}

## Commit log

2017-06-09 Update 06-09-2017
    Modified serial communications to make more sense and changed error printouts.
2017-06-09 Update 6/9/2017
    Cleaned up serial. Grayed out drop down boxes for experiment 1 if board 1 isn't selected (code is commented as only test code has been used to verify it).
2017-06-15 Add files via upload
    The important files to have to view the basic schematic are
    Capstone_Motherboard.pro
    Capstone_Motherboard.kicad_pcb
    Capstone_Motherboard.sch
    AD5272.lib
    arduino_shieldsNCL.lib
    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
    [5V-.sch, Capstone_Motherboard-B.Cu.gbl, Capstone_Motherboard-B.Mask.gbs, Capstone_Motherboard-B.SilkS.gbo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]
2017-06-15 Updated Serial
    I'm not certain anything actually changed but better safe than sorry. We played around with the boardid pins and made changes to the communications
2017-06-15 6/15/2017 Update
    Made all drop-downs for all available daughter boards gray until appropriate boardID was found.
2017-06-19 Add files via upload
    Userfriendliness fix. Users cannot change drop down menus of any board that is not currently connected
2017-06-19 Add files via upload
    Arduino:
    1. Added SoftI2CMaster to our files so it does not have to keep being downloaded.
    2. Arduino now sends GUI raw value of id pins it reads.
    GUI:
    1. Fixed bugs including when board is 00000000 it glitching out and more.
    2. Fixed up update
2017-06-19 Arduino Update 6/19/2017
    Code now uses Arduino analog pins for digital read.
2017-06-20 Uploaded files with basic connector schematic
    [RLS.kicad_pcb, RLS.sch]
2017-06-22 Updated schematic
    [RLS.sch]
2017-06-23 06-23-2017 Update
    Updated the scope probe network to it's own screen
    Changed the connector setup
    Fixed mirrored logic analyzer pins
    Created voltage divider network for voltmeter
    [RLS.sch, Scope_Probe_Gain.sch, Voltage_Divider.sch]
2017-06-27 06-27-2017 Changes
    Added positive and negative linear regulators (LT1963 and LT3015)
    Added positive and negative regulator schematics (just placed items, still need to label everything)
    [Negative_Regulators.sch, Positive_Regulators.sch, RLS.sch]
2017-06-27 Daughter Board Connector
    Created the daughter board footprint file
    Added daughter board footprint to PCB
    [RLS.kicad_pcb]
2017-06-28 Arduino update 6/28/2017
    Added a function to send in appropriate potentiometer resistor values from requested daughterboard Vin.
2017-06-29 digital pot test done given resistance input
2017-07-01 Arduino Update 7/1/2017
    Updated for Andrew.
2017-07-02 Updated Regulator Circuits and Fixed Velleman Gain
    [Positive_Regulators.sch, RLS.sch, Scope_Probe_Gain.sch, Voltage_Divider.sch]
2017-07-03 Updated Schematic (Almost Done)
    Finished both variable regulator circuits, added connectors for LAs, added +/- 5 regulated circuit for DB +/- 5V (needs to be tested before PCB implementation), various renaming and labeling
    [+5V_-5V_Regulator.sch, Logic_Analyzer_Circuit.sch, Negative_Regulators.sch, Positive_Regulators.sch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]
2017-07-04 Updated schematic (Complete)
    Added fan circuit, updated +/- 5V regulated to have 1K pots. Next step is to truly begin the PCB. Will try to have completed by Friday. This will affect our schedule, but we can make up for it in ord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
    [+5V_-5V_Regulator.sch, ADC_Divder_&_DC_Fan.sch, ADC_Divder_Fan_Circuit.sch, RLS.sch]
2017-07-06 Most Footprints Added
    [+5V_-5V_Regulator.sch, ADC_Divder_&_DC_Fan.sch, Logic_Analyzer_Circuit.sch, Negative_Regulators.sch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]
2017-07-07 Created Molex Pin Footprint
    [+5V_-5V_Regulator.sch, ADC_Divder_&_DC_Fan.sch, ADC_Divder_Fan_Circuit.sch, Logic_Analyzer_Circuit.sch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]
2017-07-07 PCB has begun
    I also realized that I created a duplicate folder now in the GitHub...
    [+5V_-5V_Regulator.sch, ADC_Divder_&_DC_Fan.sch, Logic_Analyzer_Circuit.sch, Negative_Regulators.sch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]
2017-07-07 Fixed Andrews Mistake
    Moved the RLS folder from the master to the Schematic folder.
    [+5V_-5V_Regulator.sch, ADC_Divder_&_DC_Fan.sch, ADC_Divder_Fan_Circuit.sch, Logic_Analyzer_Circuit.sch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]
2017-07-07 Removed duplicate folder
    Removing duplicate folder Andrew created. Merged the schematic folder back where it should be for RLS.
    [+5V_-5V_Regulator.sch, ADC_Divder_&_DC_Fan.sch, ADC_Divder_Fan_Circuit.sch, Logic_Analyzer_Circuit.sch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]
2017-07-07 Arduino Update 7/7/2017
    Created and commented negative and positive regulator classes as well as the digital potentiometer class.
2017-07-08 Added buffers simulation
    Created simulation file for testing the voltage divider with the buffers and inverter.
2017-07-08 CHANGE EVERYTHING
    [RLS.kicad_pcb]
2017-07-10 Lots of changes
    Completed Schematic
    1/3 Done PCB
    Multisim file for testing ADC protection and buffer circuit
    [+5V_-5V_Regulator.sch, ADC_Divder_&_DC_Fan.sch, Logic_Analyzer_Circuit.sch, Negative_Regulators.sch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]
2017-07-11 Continued PCB and Final Schematic
    [+5V_-5V_Regulator.sch, Negative_Regulators.sch, Positive_Regulators.sch, RLS.kicad_pcb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]
2017-07-12 Arduino Update 7/12/2017
    Added the tested and fixed regulator/potentiometer code. Removed potentiometer testing arduino files.
2017-07-12 PCB Layout 90% Done
    All that is remaining is the LA traces (moved them and forgot to re-do them) and the SPI and SHDN lines for the digital pots and regs.
    Also, do not merge this branch if you can. Have it fully replace the previous folder. There were obsolete files that I removed that Github keeps because it's dumb.
    [+5V_-5V_Regulator.sch, ADC_Divder_&_DC_Fan.sch, Logic_Analyzer_Circuit.sch, Negative_Regulators.sch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]
2017-07-13 Finished PCB but...
    Somehow managed to break the schematic file. I know how to fix it, but it is tedious and pointless for now (one has to go through every single individual component and verify that it is the same in t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
    [+5V_-5V_Regulator.sch, ADC_Divder_&_DC_Fan.sch, Negative_Regulators.sch, Positive_Regulators.sch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]
2017-07-18 Arduino Update 7/17/2017
    Added/changed to the linear regulator code for simple usage with the daughterboard Arduino code.
2017-07-18 Removed clutter and unused components
    Removed
    AD5272 (not used)
    R70-5d1-3 (not used)
    Extraneous libs and misc files
    [ADC_Divder_Fan_Circuit.sch, RLS.csv, RLS.xlsx, Voltage_Divider.sch]
2017-07-18 Added Things and Fixed Schematic
    Added pots to schematic and pcb for adc balancing.
    Fixed the component annotation and netlist in the pcb.
    Shrunk the pcb down a bit.
    [+5V_-5V_Regulator.sch, ADC_Divder_&_DC_Fan.sch, Logic_Analyzer_Circuit.sch, RLS.kicad_pcb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]
2017-07-18 MAJOR CHANGE! READ BELOW
    Due to layout issues, I changed the pins used for the variable regulator shutdown lines. +V1_SHDN is now AA9, +V2_SHDN is now AA8, -V1_SHDN is now AA11, and -V2_SHDN is now AA10. MAKE SURE TO CHANGE 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
    Included in this upload is the pre-design review finish PCB and Schematic, with pdf files of each for printing and easy reference.
    [+5V_-5V_Regulator.sch, ADC_Divder_&_DC_Fan.sch, Logic_Analyzer_Circuit.sch, Negative_Regulators.sch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]
2017-07-20 Finished PCB Need to do Gerbers
    It needs to be bought
    [RLS.kicad_pcb, RLS.sch]
2017-07-21 Made a few minor changes...
    To the PCB. Also added the gerber files and fixed/added objects for the 3D visualization
    [RLS-B.Mask.gbr, RLS-B.Paste.gbr, RLS-B.SilkS.gbr, RLS-Back.gbr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]
2017-07-28 Arduino Update 7/28/2017
    Changed daughter board Arduino code to utilize the programmed linear regulators. Removed unnecessary function calls and added new calls for better interfacing between the Arduino and the GUI.
2017-07-31 Arduino Update 7/31/2017
    Cleaned up extraneous comments. Ready to be tested with motherboard.
2017-08-01 Checked against hardware
    Modified code to control linear regulators on motherboard.
    Solved digital pot communication problem.
    Confirmed GUI, motherboard, and Arduino communication successful.
    Huge milestone in the project. We have officially achieved our desired result from all linear regulators, from all boardID connectors.
2017-08-02 Arduino Update 8/1/2017
    Added code to set the oscilloscope probe gain to X1 on Arduino setup.
2017-08-02 Arduino Update 8/2/2017
    Fixed checkShutdowns() function to trigger on "11111111" string when no board is connected as opposed to "00000000".
2017-08-17 Arduino added db10
2017-08-17 Arduino Update 8/17/2017
    Updated and added additional comments and cleaned up the code.
2017-08-17 Finalized deliverables
    Removed unused visual basic code to remove confusion
    Removed legacy kicad files.
    restored schematic file from history. Did this because a problem was discovered with an update I pushed. (Oops, but this is why we're using Github.)
    [+5V_-5V_Regulator.sch, 5V-.sch, ADC_Divder_&_DC_Fan.sch, Bill of Materials for Motherboard and System.xlsx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]
2017-08-18 Completed db10 arduino stuff
